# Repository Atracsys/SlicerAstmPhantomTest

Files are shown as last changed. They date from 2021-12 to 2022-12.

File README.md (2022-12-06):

# ASTM Phantom Test
This software is a module for [3D Slicer](https://www.slicer.org) to perform the accuracy test of a tracking system as described in the [standard ASTM F2554](https://www.astm.org/f2554-22.html) in its latest version (2022).

This test relies on a calibration object, hereafter referred to as the "phantom", of known dimensions measured by a [CMM](https://en.wikipedia.org/wiki/Coordinate-measuring_machine). Performing measurements on such a phantom provides a reliable assessment of the tracking system accuracy and precision.

# Table of contents
- [Material](#material)
- [Required software](#requiredSoft)
   - [PLUS Toolkit](#plusInstall)
   - [3D Slicer](#slicerInstall)
- [Parameter files](#paramFiles)
   - [Pointer file](#pointerFile)
   - [Working volume file](#wvFile)
   - [Phantom file](#phantomFile)
- [Usage](#usage)
   - [Setup](#setup)
   - [Launching the software](#launch)
   - [Running the tests](#tests)
   - [Getting the results](#results)
- [Troubleshooting](#trouble)

# Material
To perform the test, the following items are necessary:
- [ ] A **phantom** with a distribution of divots and a reference tracked array rigidly attached. See the [standard](https://www.astm.org/f2554-18.html) for requirements and recommendations regarding phantom design and manufacturing.
- [ ] The tested **tracking system**, typically including
  - [ ] A **pointer** composed of a tracked array and a shaft with a pointy end fitting the divots.
  - [ ] A **tracker** which spatially locates the various arrays aforementionned. Various technologies can be utilized (optical, magnetic, etc).
  - [ ] A **computer** to receive and analyze the tracking data. The present software is to be installed on this computer, alongside the various supporting tools and libraries. Since this software also provides visual guidance to perform the test, a computer monitor is recommended.

# Required software
## PLUS Toolkit
[PLUS Toolkit](https://plustoolkit.github.io/) is a free, open-source set of software tools for Computer-Assisted Surgery, which includes a wrapper for SDK's from many manufacturers of tracking systems. This enables a standardization of the tracking data streaming from the tracker to the computer, thanks to an [OpenIGTLink](http://openigtlink.org) server (i.e. the **Plus Server**).

### Installation
Pre-built installers for more than twenty systems are available for Windows from the [Download page](https://plustoolkit.github.io/download.html). To know which installer to choose, the user may refer to the table at the bottom of that page. The version must be 2.9.0.202207x or more recent. Since the 2.9 release is not stable yet, one can access it from the [Latest Development Snapshot](http://perk-software.cs.queensu.ca/plus/packages/nightly).

:warning: Beside the wrappers, PLUS Toolkit also includes the SDK for most systems. For Atracsys trackers though, the SDK needs to be installed separately on the computer. Also, the Atracsys SDK version is required to be 4.5.2 or more recent.

To install on Linux or Mac OS, please refer to the [Developer's guide](https://plustoolkit.github.io/developersguide).

### Configuration file
The **Plus Server** relies on a configuration file, in XML format, to set the tracking parameters. These configuration files are located in `/config` for pre-built versions and in `/PlusLibData/ConfigFiles` for compiled versions. Plus Toolkit already comes with two examples of configuration file for the ASTM Phantom Test: one for Atracsys trackers (`PlusDeviceSet_Server_AstmPhantomTest_Atracsys.xml`) and one for NDI Polaris trackers (`PlusDeviceSet_Server_AstmPhantomTest_NDI_Polaris.xml`). The user is welcome to duplicate and customize these configuration files to meet their needs, but some parameters, listed below, must be correctly set in order to successfully run the ASTM Phantom Test.

* `Device > Type` describes what tracker is used and must be in accordance with the version of PLUS Toolkit installed. For more information on what type to use, please refer to the [Configuration page](http://perk-software.cs.queensu.ca/plus/doc/nightly/user/Configuration.html).

* The `Device > ToolReferenceFrame` gives a name to the reference frame of the tracking coordinates, typically the tracker.

* `DataSources` provides the inputs i.e. the description of the tracked arrays. For our ASTM Phantom Test, two are necessary:
  - the array attached to the phantom with the id `Phantom`. This id must remain unchanged.
  - the array of the pointer with the id `Pointer`. This id must remain unchanged.
  Each array can be for `ACTIVE` tracking (with emitting markers) or `PASSIVE` tracking (with reflective markers). `GeometryFile` is set as the path (relative to the xml configuration file) of the geometry of the array (which enables the detection and tracking). For Atracsys trackers for example, the geometry is contained in an .ini file as such:
  ```ini
  [geometry]
  count=4
  id=101
  [fiducial0]
  x=-24.3012
  y=-29.5377
  z=0.14917
  [fiducial1]
  x=-66.7241
  y=14.0559
  z=-6.80029
  [fiducial2]
  x=20.8942
  y=3.55241
  z=1.4325
  [fiducial3]
  x=70.131
  y=11.9294
  z=5.21875
  ```
  However, each manufacturer has its own format for geometry files (e.g. NDI uses binary ROM files), so please refer to the tracker's manual for more information.

* The `OutputChannel` will be composed of the two streams of our `DataSources` so `Phantom` and `Pointer`

* The Plus Server is an OpenIGTLink server, which sends messages of type `TRANSFORM`. These represent 4x4 matrices describing the transform from one item to another. For the ASTM Phantom Test, we need three transforms:
  - the transform from the pointer (`Pointer`) to the phantom (`Phantom`), which results in `PointerToPhantom`
  - the transform from the phantom (`Phantom`) to the tracker (`Tracker`), which results in `PhantomToTracker`
  - the transform from the pointer (`Pointer`) to the tracker (`Tracker`), which results in `PointerToTracker`
  <br>**DO NOT** change the names of the output transforms, as these are hardcoded in the Slicer module.
  
  The option `SendValidTransformsOnly` has to be set to `FALSE`, which helps the device detect when an item gets out of tracking (the corresponding transform attribute then goes from "VALID" to "MISSING").

* Other device-specific parameters can be set, depending on the manufacturer and/or the tracker. For example, the origin of the tracker coordinate system is supposed to be at the center of the device. For Atracsys trackers, the device parameter `SymmetriseCoordinates="1"` is then required to move the origin of the tracker from the left camera to the center.

For a better understanding of Plus configuration files, their structure is detailed in the [Configuration page](http://perk-software.cs.queensu.ca/plus/doc/nightly/user/Configuration.html) of the User Manual.

## 3D Slicer
[3D Slicer](https://www.slicer.org) (or "Slicer" for short) is a free, open-source software dedicated to medical image analysis. One of strengths of Slicer is its modularity, as it is possible to develop extensions to further expand its features or use its platform to create a dedicated software. The latter is the approach chosen for this project. Our Slicer module sets up an **OpenIGTLink client**, connects to the **Plus Server** and receives and analyzes the tracking data to perform the ASTM Phantom Test.

### Installation
From Slicer's [download page](https://download.slicer.org), download and install the latest stable release corresponding to the computer OS (5.0.3 or above). Then, run Slicer and click on `Install Slicer Extensions` from the welcome panel.

Launch extensions manager

In the Extensions Manager, head to the `Install Extensions` tab (1) and browse or look for the `AstmPhantomTest` extension (2). Once found, simply click on Install (3) and restart Slicer as required (4).

Module install

The ASTM Phantom Test module is now installed and a shortcut for it can be set in the main menu bar by returning to `Application Settings` > `Modules`.

Module shortcut

### Keeping the module up-to-date
It is important to keep the module up-to-date in order to benefit from future improvements and bug fixes. Thus, it is recommended to set Slicer to automatically check (and even install) module updates for you. To do this, head back to the Extensions Manager, click on the wrench icon (1) and check the desired options (2).

Automatic update

Doing so, updates will be notified as a yellow dot on the Extensions Manager button (see below on the left). Browsing the extensions will then show you a restart prompt but also offer the possibility to cancel the update (see below on the right).

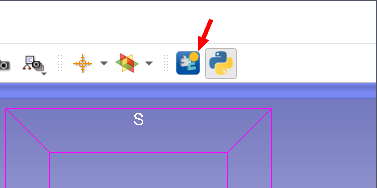
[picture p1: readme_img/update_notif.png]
Update notification
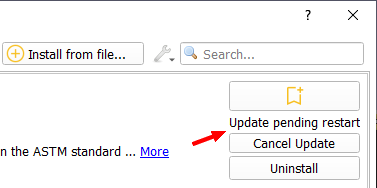
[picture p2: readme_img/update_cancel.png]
Update cancel
 

If you want to manage the updates yourself, you can also manually check and install the update from the Manage Extensions tab (1), click on `Check for updates` (2) and if an update is available, it will show up along with an `Update` button (3).

Manual update

:warning: Updating the module will require to restart Slicer to take effect.

# Parameter files
The module relies on several parameter files to accomodate for the used hardware. Those parameter files may be duplicated and customized to accomodate for specific tools or requirements. The parameter files are located in the module folder, whose path (hereafter coined `module_path`) can be found via `Application Settings > Modules`.

Module path

## Pointer file
Located in `module_path\Resources\ptr`, this parameter file contains the maximum tilt angle (`MAXTILT`, in degrees) beyond which the pointer manufacturer does not guarantee tracking.
This value typically depends on the type of tracking technology and that of the fiducials/markers attached to the pointer.
The parameter file also describes the pointer rotation axes (`ROLL`, `PITCH`, `YAW`) **in the coordinate system of the pointer**. :warning: These axes need to match those set for the [working volume](#wvRotAxes) (see example in the [Troubleshooting section](#tbWrongOrientation)).
Finally, the file contains the pointer height (`HEIGHT`, in mm) to accomodate for pointer tracking while the phantom nears the top of the working volume. This consists in placing the top target location for the phantom ([`TL`](#wvFile)) with a downward offset of `HEIGHT` + the elevation of the highest divot (e.g, #47) from the central divot ([`CTR`](#phantomFile)). If `HEIGHT` is set to 0, then there is no compensation.

## Working volume file
Located in `module_path\Resources\wv`, this parameter file contains various information:
- the coordinates of the various locations that the phantom should be placed at in the working volume. Beside the center location (`CL`), all other locations lie at the edges of the working volume, as described in the ASTM standard. The four other locations are placed on the outer boundaries of the back plane. `BL` is located at the bottom, `TL` at the top, `LL` at the left and `RL` at the right. All these coordinates are expressed in the referential of the tracker.

Locations
Locations

- the actual working volume is described by the `NODES` coordinates (again in the tracker referential frame). The working volume is assumed to be composed of a succession of quadrilateral planes, but their number can vary.

Nodes
Nodes

- the moving tolerance is the threshold that separates actual pointer motion from the slight "wiggle" that typically occurs with most tracking technologies even when the pointer tip is static. Since the magnitude of this wiggle often depends on the distance to the tracker, the range for the moving tolerance is given by two extreme values. `MOVTOLMIN` sets the minimum threshold when the pointer is the closest possible to the tracker (e.g, 0.4mm at 920mm in depth) and `MOVTOLMAX` the maximum when the pointer is the farthest possible (e.g, 1.0mm at 2850mm in depth). The **moving tolerance is automatically set by the module** during the tests within the provided range. Nonetheless, if the user experiences trouble acquiring a divot because the program keeps detecting tip motion when there is none, the moving tolerance can be manually increased live (see [troubleshoot](#tbRemainingStatic)).

- the working volume file also describes the pointer rotation axes (`ROLL`, `PITCH`, `YAW`) **in the coordinate system of the tracker**.  :warning: These axes need to match those set for the [pointer](#ptrRotAxes) (see example in the [Troubleshooting section](#tbWrongOrientation)).

- the model name of the tracker (`MODEL`) is also given in the working volume file. The name has to match one of the models included in `module_path\Resources\models`. For example, `MODEL = ftk500` will prompt the software to load the 3D model `ftk500_RAS.stl`.

## Phantom file
Located in `module_path\Resources\gt`, this parameter file describes the divots on the phantom and their use. All the divots coordinates are listed (`POINT id`,`X`,`Y`,`Z`) and given **in the referential frame of the phantom**. This referential frame is defined by the first three divots provided by `REF` in the following order O, X and Y.

The sequence of divots used for the multi-point test is given by `SEQ` and the id of the central divot (used for all the other tests) is given by `CTR`.

```
REF = 1 19 18
SEQ = 20 18 12 6 1 7 13 19 25 22 28 30 32 34 37 35 40 42 44 46
CTR = 20
MODEL = phantom2022

POINT 1
X 0.00
Y 0.00
Z 0.00
POINT 2
X 0.01
Y 14.44
Z 0.00
POINT 3
X 14.45
Y 0.00
Z -0.01
...
```

The model name of the phantom (`MODEL`) is also given in the parameter file. The name has to match one of the models included in `module_path\Resources\models`. For example, `MODEL = phantom2018` will prompt the software to load the 3D model `phantom2018_RAS.stl`. Two models are already included, corresponding to the last two revisions of the standard from 2018 and 2022.

# Usage
## Setup
The tracker and the phantom are set up so that:
1. the tracker is installed according to the manufacturer's specifications (typically in orientation). Then, it is connected to the computer and turned on. For more details about this connection (e.g. cabling, network configuration, drivers), please refer to the tracker manual.
2. the phantom is inially placed within the first half of the working volume facing the tracker.
3. during most measurements, both the phantom and the pointer must keep their tracked array (approximately) oriented towards the tracker so as to ensure an optimal tracking accuracy. The only exception for the pointer is during the rotation tests. The only exception for the phantom is during the single point tests with extreme orientations.
4. the operator can manipulate the pointer with respect to the phantom with ease, without occluding the device lines of sight. The operator should also be able to monitor the progress of the tests on the screen monitor. See example of setup below.
5. if possible, sound should be enabled on the computer as audio clues are given to signal progression during the tests, which sometimes alleviates the need to look at the screen (especially during the multi-point test).

Example of setup
Example of setup

## Launching the software
### Plus Server
The Plus Server is launched by running `PlusServerLauncher.exe` from the `bin` repository of PLUS Toolkit.

Once launched as illustrated below, the path to the configuration files folder (1) is automatically selected as the one included in the PLUS Toolkit repository. If the requested configuration file is located elsewhere, the user may manually select another folder and refresh it thanks to the two buttons next to the input field.

Then, the user shall select from the dropdown menu (2) the appropriate configuration file, correctly formatted as explained in the [Configuration file](#configFile) subsection. Finally, the server is launched by click on the `Launch Server` button (3) and the message `Connecting to devices.` appears.
 
Server Launcher

If the server has sucessfully started, it appears as shown below.

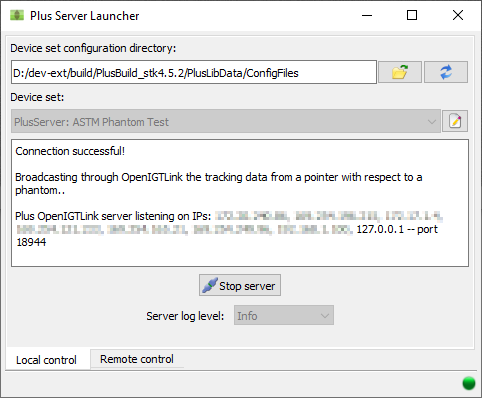
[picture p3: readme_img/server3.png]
Server Launcher Connected


### Slicer
Start Slicer by clicking a shortcut to it. If no shortcut to Slicer was created during its installation, the application may still be launched by running the `Slicer` executable from its repository.

Once Slicer is started, the ASTM Phantom Test module can be accessed via the dropdown menu in the `Tracking` category or via the shortcut in the menu bar (if [previously created](#moduleShortcut)).

Module access

## Running the tests
### Preliminary steps
When the module starts, a dialog window pops up and the user has to select the folder where the [output files](#results) (including the log) will be saved.

On the left panel, the tracking status of the pointer and the reference array (attached to the phantom) is displayed. These labels correspond to the three [transforms streamed](#transformsStream) by the Plus Server and show up either as `OK` or `MISSING`.

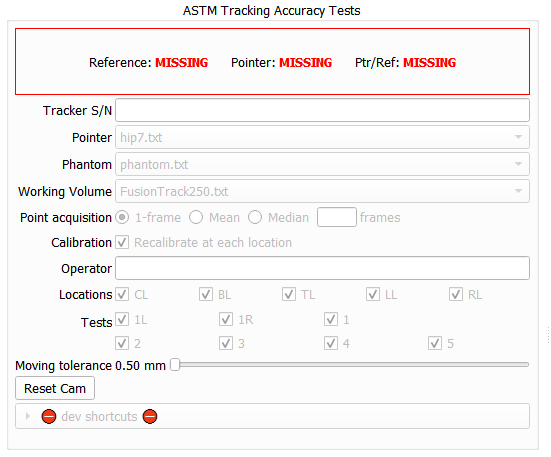
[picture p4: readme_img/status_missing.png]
Status missing


The program won't start until both the pointer and the phantom reference array are being tracked (even briefly), i.e. until all transforms are displayed as `OK`.

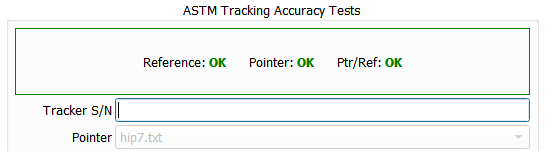
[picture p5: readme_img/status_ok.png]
Status ok


Once the program is started, the working volume and the target locations are previewed from the top and the front of the scene. The choice in working volume may be changed while [setting the parameters](#parameterSetting) in the left panel.

Top and front views

The first parameter the operator is expected to input is the tracker serial number (1).

Parameter input 1

Once filled in, the other parameters are unlocked and the user can choose the appropriate [pointer file](#pointerFile) (2), [phantom file](#phantomFile) (3) and [working volume file](#wvFile) (4). The user may also choose the [point acquisition mode](#ptAcquiMode) (5), the recalibration option (6) and has to input his id in the `Operator` field (7).

Parameter input 2

There are **three point acquisition modes** available:
- **1-frame**: the point coordinates are those measured in a *single frame* in the middle of the acquisition. In this mode, the acquisition length is set to 0.5 sec.
- **mean**: the point coordinates are the *mean* of those measured across *N* frames (default is 30). In this mode, the point acquisition lasts *N* frames.
- **median**: the point coordinates are the *median* of those measured across *N* frames (default is 30). In this mode, the point acquisition lasts *N* frames.

The option of **Recalibrate at each location** is also offered, which implies that a new calibration be performed at each selected location in the working volume. If this option is not checked, the initial calibration will be used for the remainder of the procedure. Note that, as per the standard, recalibrations are **not required but recommended**.

Filling in the operator id triggers the **initial phantom calibration**, which estimates the geometrical relationship between the coordinate system of the phantom (and thereby its divots) and the reference array attached to it. To perform the calibration, the user needs to successively pick all the divots indicated in the [phantom file](#phantomFile) by `REF` with a minimum of three divots (more can be added beyond the first three defining the [phantom coordinate system](#phantomCoordSystem)).

|For any **point acquisition**, the targets are indicated by a red sphere and their id. Once the pointer hit the target (the correct divot), the point acquisition starts, indicated by the target becoming smaller and greener. The duration of the acquisition depends on the [point acquisition mode](#ptAcquiMode). The point acquisition is done when the target becomes large and green, and a "pop" sound is played. Removing the pointer from the divot then prompts the program to show the next target, if any. Removing the pointer before the point acquisition is done will reset the current target.|
|---|

Calibration

Once the calibration is over, the choice in locations is unlocked (8). By default, all [five locations](#wvFile) in the working volume are enabled as recommended by the standard, but the user can, at any time during the session, disable and skip undone locations if desired. Likewise, by default all seven tests are enabled (9) as recommended by the standard, but the user can disable certain tests **before** the phantom hits a target location in the working volume.

The [moving tolerance](#movTol) slidebar (10) allows the user to monitor and adjust the sensibility to pointer motion. Finally, the operator may interact with the 3D scene with the mouse and the optimal view can be automatically reset with the `Reset Camera` button (11).

Locations & tests

To **start the tests**, the user must first place the phantom at one of the designated locations in the working volume. To help the user in this task, the interface switches back to "working volume guidance". In the top and front views (left and right respectively), the user can now see where the phantom is located with respect to the target locations. Once the phantom is stabily placed at one of the enabled locations, a specific sound is played and the first test starts.

Working volume guidance

### Single Point Tests
Referred to as the *Single Point Accuracy and Precision Test* in the ASTM standard, this test aims at assessing the performance of the tracking system for single point measurements. To do so, the user must repeatedly acquire the central divot for a certain number of times. The progression of the test is displayed in the top right corner.

The single point test is to be performed with three different phantom orientations: `Extreme Left`, `Extreme Right` and `Normal`. The two extreme orientations correspond to the most extreme left and right rotations of the phantom while maintaining tracking of the attached reference element. The normal orientation is with the phantom rotated such that the attached reference element is optimally located by the tracker.

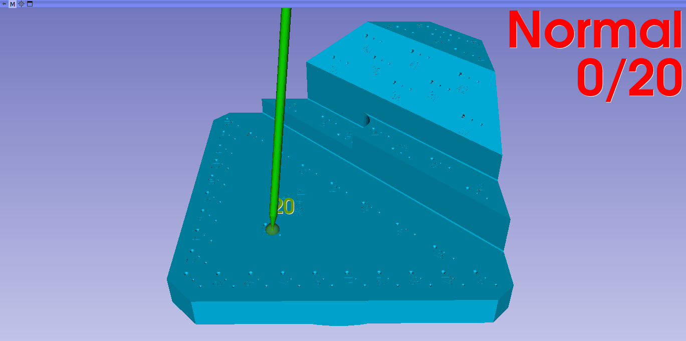
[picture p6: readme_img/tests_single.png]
Single point test


### Rotation Tests
As described in the ASTM standard, these *Rotation Tests* aim at assessing the stability in measurement of a single point while the pointer rotates around specific axes (roll, pitch, yaw). The definition of these axes are defined in the [pointer file](#pointerFile) and in the [working volume file](#wvFile) in their respective coordinate system.

<p float="left">
  
   
  
</p>

To start the test, the user must lodge the pointer in the central divot, which will toggle the display of the pointer angles with respect to each rotation axes. The current rotation axis to be measured is highlighted by the symbols > and <. The pointer must be **rotated only around that specific axis**, i.e. the other angles shall remain as close to 0 as possible during the test.

To start the actual measurements, the user must first rotate the pointer as detailed above until it is not tracked anymore. Then, performing a counter rotation, the pointer is tracked again, which will trigger the program to begin saving the measurements. The user shall continue rotating that way until they reach the opposite end of the angular range, i.e. until the tracking stops again, which will stop the measurements.

This routine is to be repeated for each axis corresponding to the [enabled rotation tests](#enableTests) in the parameter panel.

|Certain rotations may lead to the pointer colliding with parts of the phantom or escaping the divot before it gets out of tracking. It is preferable to prematurly stop the measurements (and hence the rotation test) slightly before reaching these dead-ends. To artificially set the pointer out of tracking, swiftly occlude the pointer with the hand while remaining in the central divot.
|---|

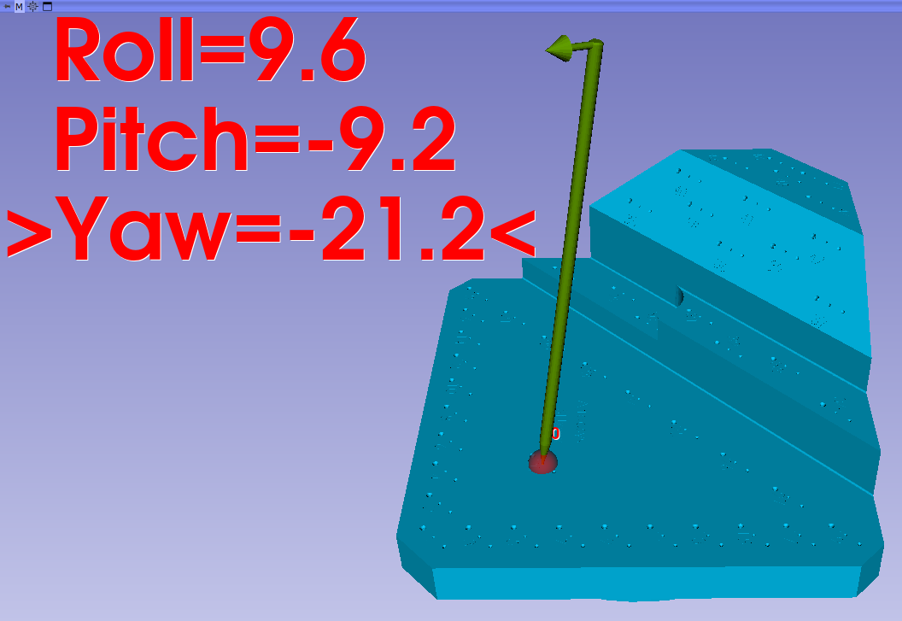
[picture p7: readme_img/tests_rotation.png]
Rotation test


### Multi-Point Test
As explained in the ASTM standard, this test consists in picking various points on the phantom and comparing the resulting point cloud to the ground truth given by the [phantom file](#phantomFile). For a same set of acquisitions, this comparison is done in two ways: comparing point-to-point distances and actual point cloud registration. The results constitute an assessment of the accuracy of the tracking system in multi-point picking.

To perform the test, the user only needs to measure with the pointer a sequence of points, defined in the [phantom file](#phantomFile) by `SEQ`. During the test, the current target is shown in red and the acquired points become green.

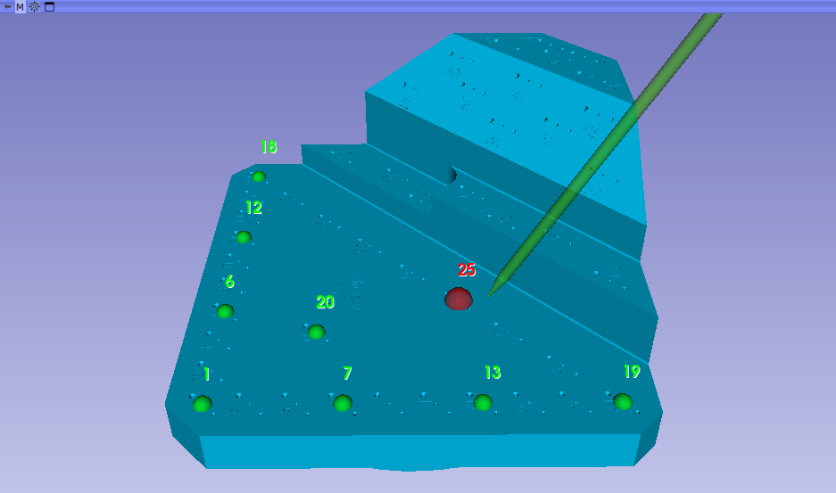
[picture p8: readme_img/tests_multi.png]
Multi-point test


## Getting the results
Once all the enabled tests for all the enabled locations are done, the program generates various files in the output folder.
- a **report in HTML** format (to be open with any internet browser), that contains all the statistical analysis of the measurements for each test.
- a **json file** containing all the parameters and the actual measurements. This is meant to perform some more analysis if desired.
- a **log file**, which contains all the events that occured during the session. The log is written in real-time, so even if the program crashes, the events are saved. The log file is common for all the sessions performed on a same day.

Besides, a Matlab script (`AnalyzePhantomJSON.m`) is also provided that parses all the recorded measurements and display the results.

# Troubleshooting

1. *I'm having trouble acquiring a divot although my pointer is static (i.e. placed in a divot).*
   - Check that there is no occlusion of any of the markers.
   - Check the environment for interferences. For optical systems, use the manufacturer's tools to visually assess in the camera images the absence of reflections that could affect the detection of the markers, typically on the phantom.
   - Increase the [moving tolerance](#movTol) by increments of 10% of the total range. If the maximum tolerance is reached, you may slightly increase that maximum value in the [working volume file](#wvFile) and restart Slicer. However, increasing the moving tolerance further will hinder the reliability of the tests.

2. *The Plus Server Launcher does not connect to my device or gives me errors.*
   - Check that the installed version of [PLUS Toolkit](#plusDownload) is the appropriate one for my system.
   - Check that the SDK version of my system is compatible with PLUS Toolkit. In doubt, you may [contact the PLUS Toolkit development team](https://plustoolkit.github.io/contact.html).
   - Check that the device is powered on and connected to the computer as per the manufacturer's guidelines.
   - Check that the computer is well configured for the tracking system as per the manufacturer's guidelines (typically network configuration if connected through ethernet).
   - Check that the [configuration file](#configFile) has been correctly written.

3. *The status for the phantom and/or the pointer remains MISSING despite being visible by the tracker.* => There is a problem of communication between Slicer and the Plus Server.
   - Check that the Plus Server is launched **with the appropriate configuration file** and successfully connected to the tracking system.
   - In Slicer, head to the Transforms module via the dropdown menu and check the Active Transform list at the top. If "PhantomToTracker" or "PointerToTracker" is missing, check that the [geometry files](#geometryFile) are correct and that their paths in the configuration file are valid.

4. *I can't naturally trigger the out of tracking of the pointer during the rotation tests.*
   - See the recommendation for [artificially ending the rotation measurements](#artifOutOfTracking) prematurly.
   
5. *The pointer is misoriented in the rendering and/or the angle values are not near 0 when "facing" the tracker.*
   - There is a mismatch between the rotation axes in the tracker's coordinate system (in the [working volume file](#wvRotAxes)) and the rotation axes in the pointer's coordinate system (in the [pointer file](#ptrRotAxes)). Those axes should be the same in the world's coordinate system and they are important as they allow for 1) a correct interpretation of the pointer rotations with respect to the tracker and 2) a correct orientation of the 3D pointer model in the display. Below is an illustrated example of rotation axes in both coordinate systems:

RotationAxes
RotationAxes

6. *I imported my own 3D models in STL format for the phantom, the pointer and/or tracker, and they are misoriented in the 3D scene.*
   - Slicer uses the [RAS convention](http://www.grahamwideman.com/gw/brain/orientation/orientterms.htm) for axes, which differs from the typical X,Y,Z spatial axes. For a correct interpretation of the STL file, it must be edited (e.g, using Notepad) and its first line shall include `SPACE=RAS`. For example, the first few lines of the STL can be:
   ```
   solid SPACE=RAS
    facet normal 0 0.987688 -0.156434
     outer loop
      vertex -150 50 0
      vertex 150 50 0
	  ...
   ```
   - Finally, the model for the pointer is not meant to be replaced. If you still want to do it, you can replace the model `pointer_RAS.stl` by the one of your choosing, but make sure that the origin and axes are the same and that the RAS space is specified as described above.

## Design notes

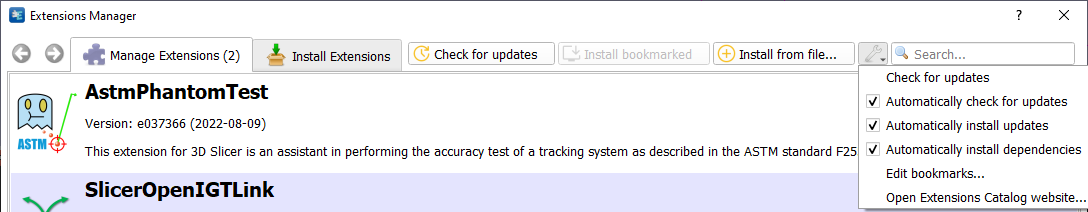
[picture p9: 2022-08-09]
readme_img/update1.png

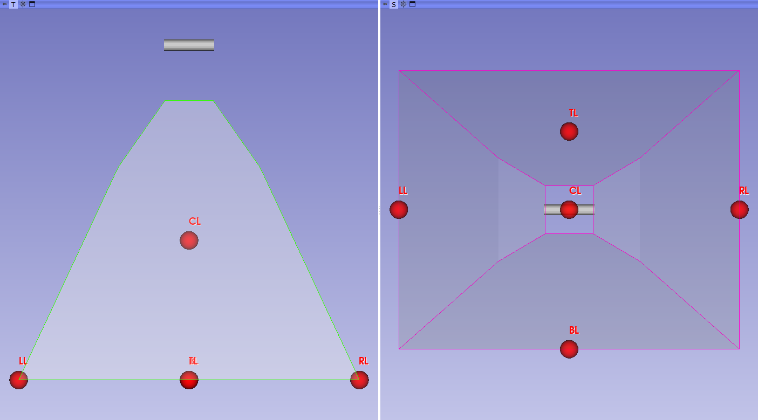
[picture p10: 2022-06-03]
readme_img/views.png

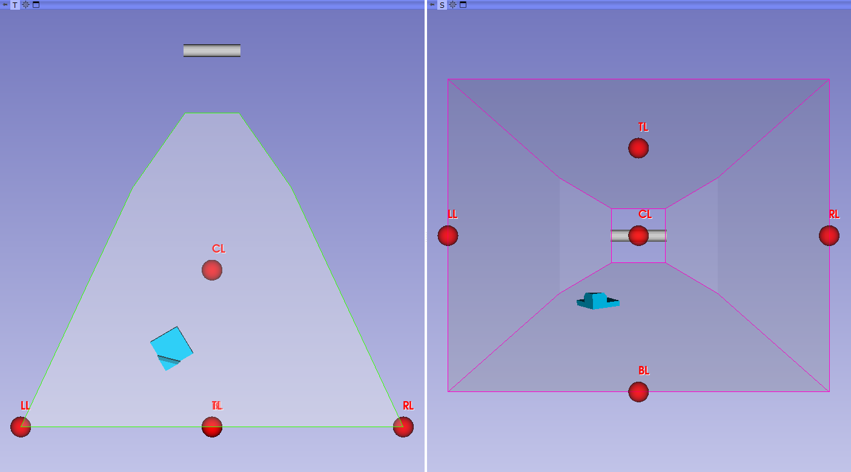
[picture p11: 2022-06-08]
screenshots/screenshot3.png

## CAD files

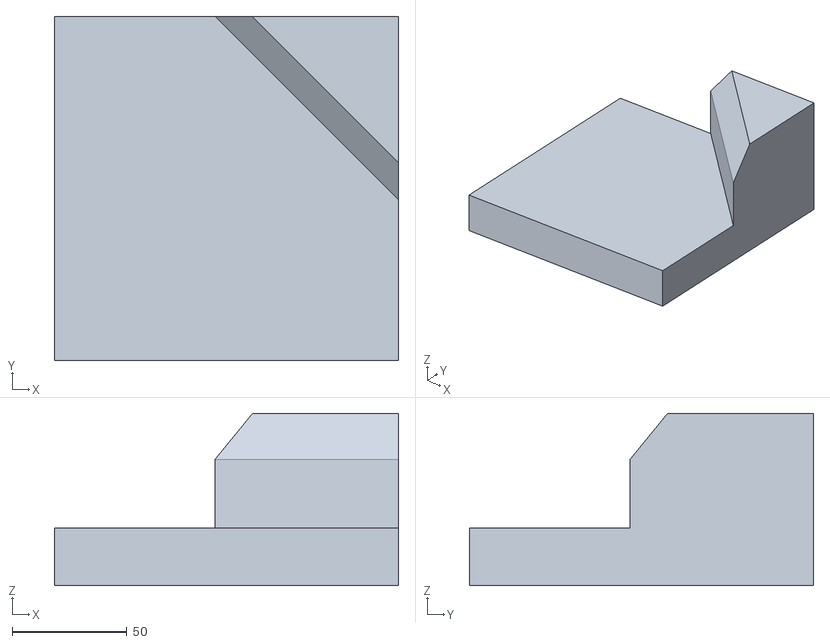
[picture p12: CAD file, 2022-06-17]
AstmPhantomTest/Resources/models/simpPhantom_RAS.stl
150.0 x 150.0 x 75.0

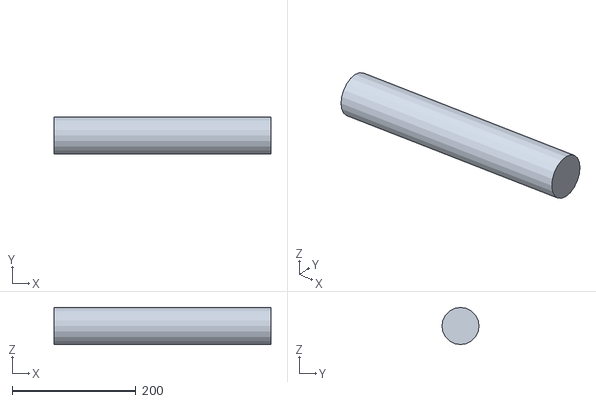
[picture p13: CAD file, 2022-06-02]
AstmPhantomTest/Resources/models/stk300_RAS.stl
350.0 x 60.0 x 60.0

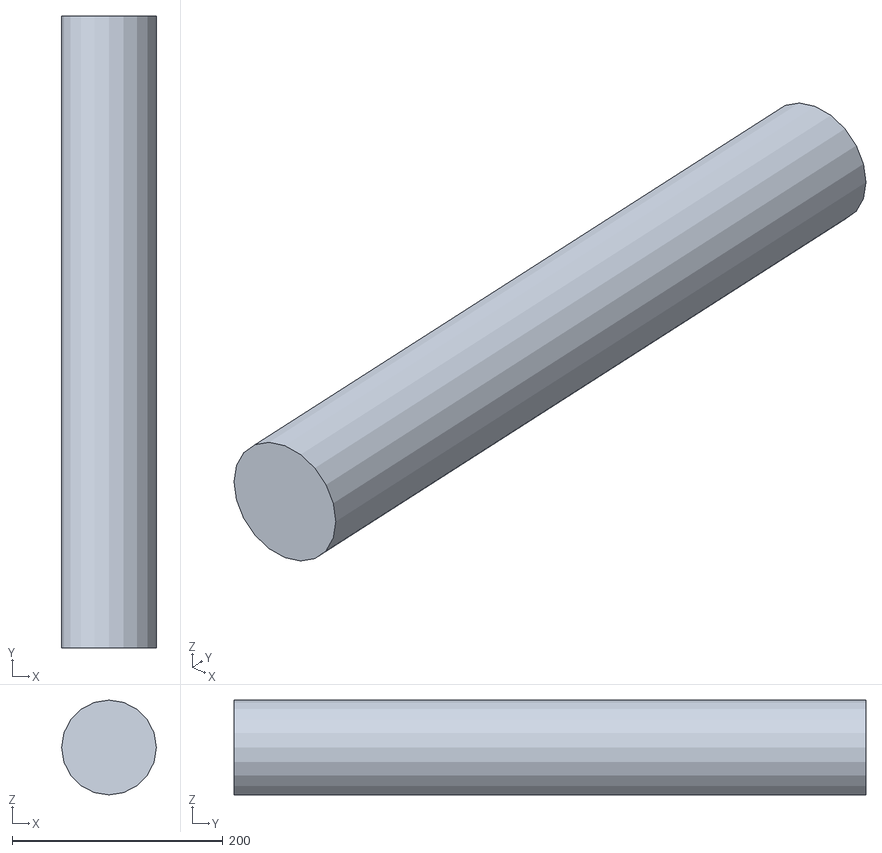
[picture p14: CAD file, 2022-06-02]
AstmPhantomTest/Resources/models/vega_RAS.stl
90.0 x 600.0 x 90.0

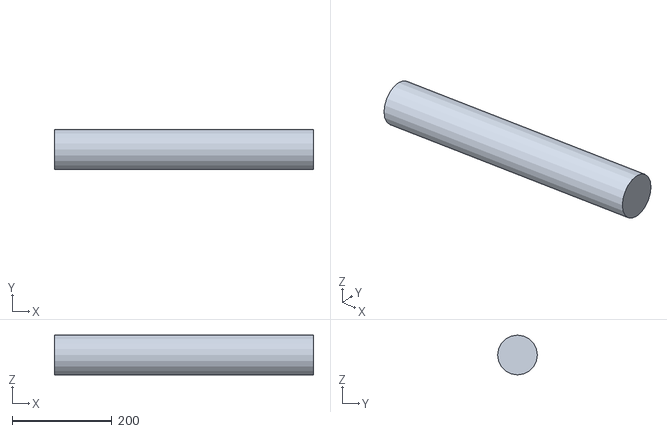
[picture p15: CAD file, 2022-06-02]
AstmPhantomTest/Resources/models/ftk500_RAS.stl
520.0 x 80.0 x 80.0

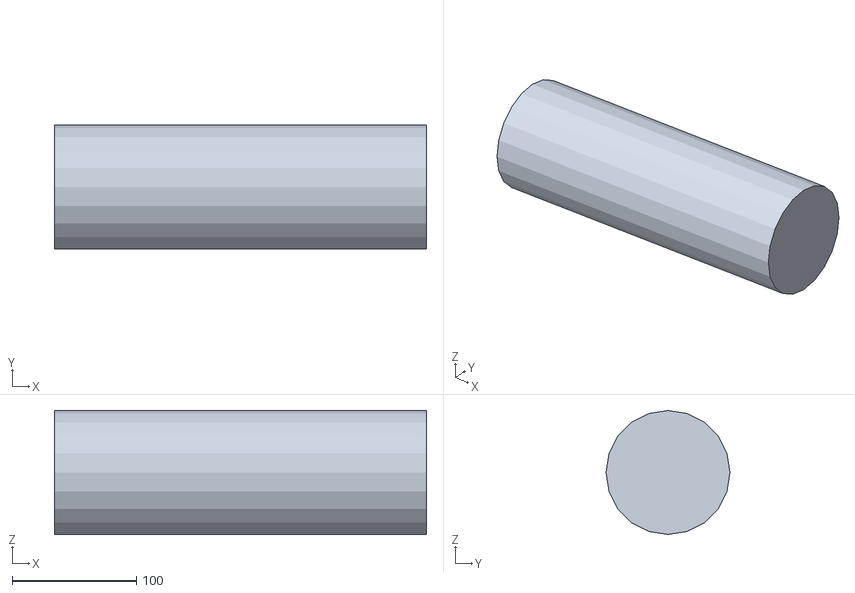
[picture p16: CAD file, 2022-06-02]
AstmPhantomTest/Resources/models/ftk250_RAS.stl
300.0 x 100.0 x 100.0

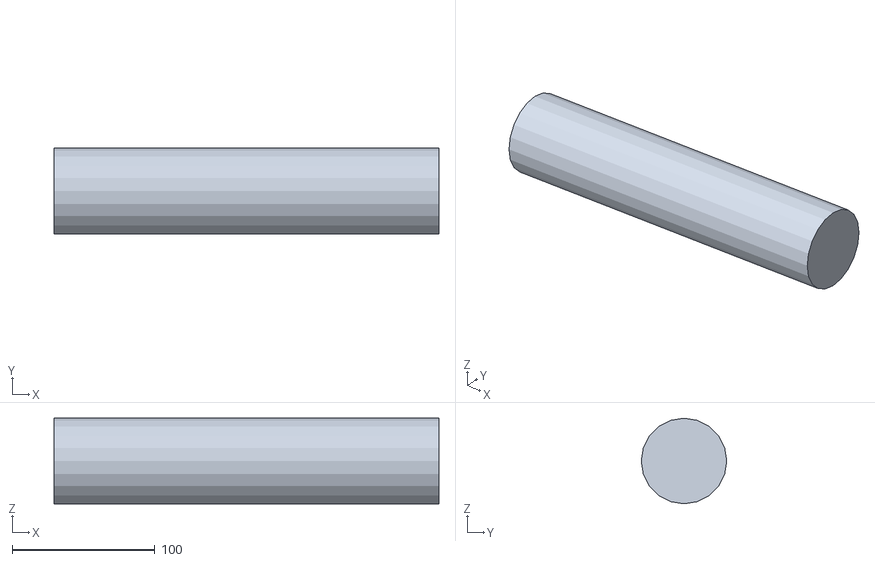
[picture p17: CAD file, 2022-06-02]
AstmPhantomTest/Resources/models/stk180_RAS.stl
270.0 x 60.0 x 60.0

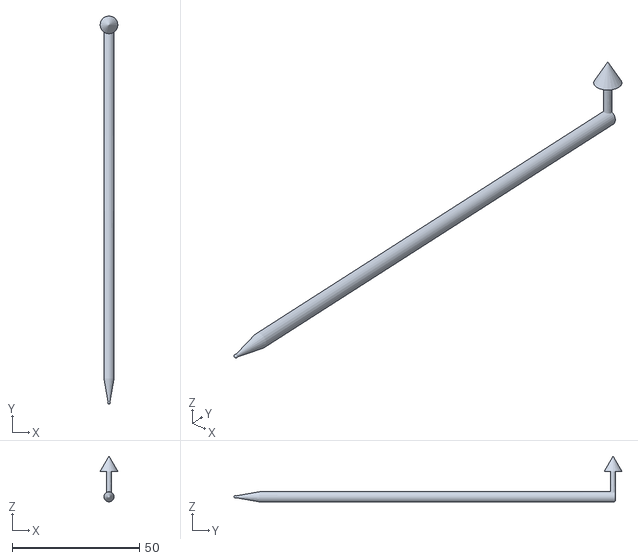
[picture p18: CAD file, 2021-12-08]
AstmPhantomTest/Resources/models/pointer_RAS.stl
7.00 x 152.5 x 18.0

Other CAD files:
AstmPhantomTest/Resources/models/simpPhantom_RAS.STL

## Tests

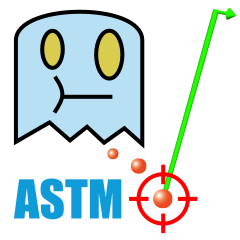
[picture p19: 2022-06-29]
SlicerAstmPhantomTest.png

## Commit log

2021-11-30 First part of ReadMe
    - Added Intro, Material and Required Software and the beginning of Usage
    - updated setup figure to accomodate for dark theme too
2021-12-08 First full module commit based on Proto3
    [pointerRAS.stl, simpPhantomRAS.STL]
2021-12-09 Improved camera placement in working volume guidance
2022-02-03 Raise number of samples for Single Point test from 10 to 20
2022-02-23 Point acquisition improved
    - Introduction of three modes: 1-frame and mean or median across a certain number of frames
    - acquired coordinates stored in Pointer class rather than Targets
    - acquisition time reduced to 500ms from 1sec
    - fixed bug that stored the point coordinates twice in the accumulator
    - small fixes
2022-05-10 Fix camera placement bug for top view
    The magnitude was not in absolute value from PBK
2022-05-25 ENH display tool status (MISSING or OK) for reference frame, pointer and pointer/reference
    Made the logic class less dependant on rendering and rendering handles
2022-06-02 Including tracker model in scene
    Each tracker has a specific model in /models as a STL file. The model is determined by MODEL in the working volume parameter file.
    [ftk250_RAS.stl, ftk500_RAS.stl, pointer_RAS.stl, simpPhantom_RAS.STL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]
2022-06-02 Reset camera now works regardless of the stage
    and the working volume is displayed as soon as the process is launched
2022-06-03 ENH Improve checkbox experience
    The current location and the current test are beautifully highlighted in green
    The operator can check/uncheck tests as long as they are not done or undergoing
2022-06-08 ENH added messages for Calibration and End Session
2022-09-26 To accomodate strong jitter:
    - PosQueue's stride no longer calculated on single frames (first and last of queue) but rather medians of first and last N frames (here N=10)
    - moving thresh now fixed at 0.5mm since the median smoothing should remove need to accomodate for larger jitter at farther locations
    - proxiThresh at 4mm to accomodate for strongly decalibrated cameras
